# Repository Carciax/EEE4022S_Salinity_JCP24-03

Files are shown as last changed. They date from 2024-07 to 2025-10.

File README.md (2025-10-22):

## The Design of a Salinity Sensor for Antarctic Research
**EEE4022S_Salinity_JCP24-03**
 
This project focused on the design of a salinity sensor for measuring the salinity of the sea water beneath the Antarctica ice caps which had a unique habitat and salinity range due to the ice caps expelling large amount of salt through brine channels into the ocean below. The project consisted of two PCB boards, a probe to be inserted through a drilled hole in the ice and a controller to calibrate, request and display measurements. The probe used a complex switching array to measure the average resistance between a pair of either gold or titanium electrodes using a voltage sweep, then it would calculate the waters conductivity, and finally its salinity.

The salinity sensor probe image

**File Structure**
- EEE4022S 2024 FINAL REPORT CLRCAM007 Clark CF - Pead: The final project report
- CAD: 3D printing files for the pressure sensor waterproof
- Code: The embedded C project code running on the controller and probe boards and the RS485 protocol between them.
- GA Forms: forms required to submit to ECSA
- PCBs: The KiCAD design files for the controller, probe and gold electrode PCBs.
- Presentation: Contains the power point and helper files for the final presentation
- Prototype: The prototype salinity sensor that preceeded this project.
- Report Helper Documents: Documents used for data processing and store from the testing of the probe.
- Report: The LaTeX project file for generating the final report.

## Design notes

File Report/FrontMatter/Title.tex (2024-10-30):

\thispagestyle{empty}
\begin{center}
    
\Huge

\vspace{5cm}

% Title
The Design of a Salinity Sensor for Antarctic Research

\vspace{1cm}

% UCT logo
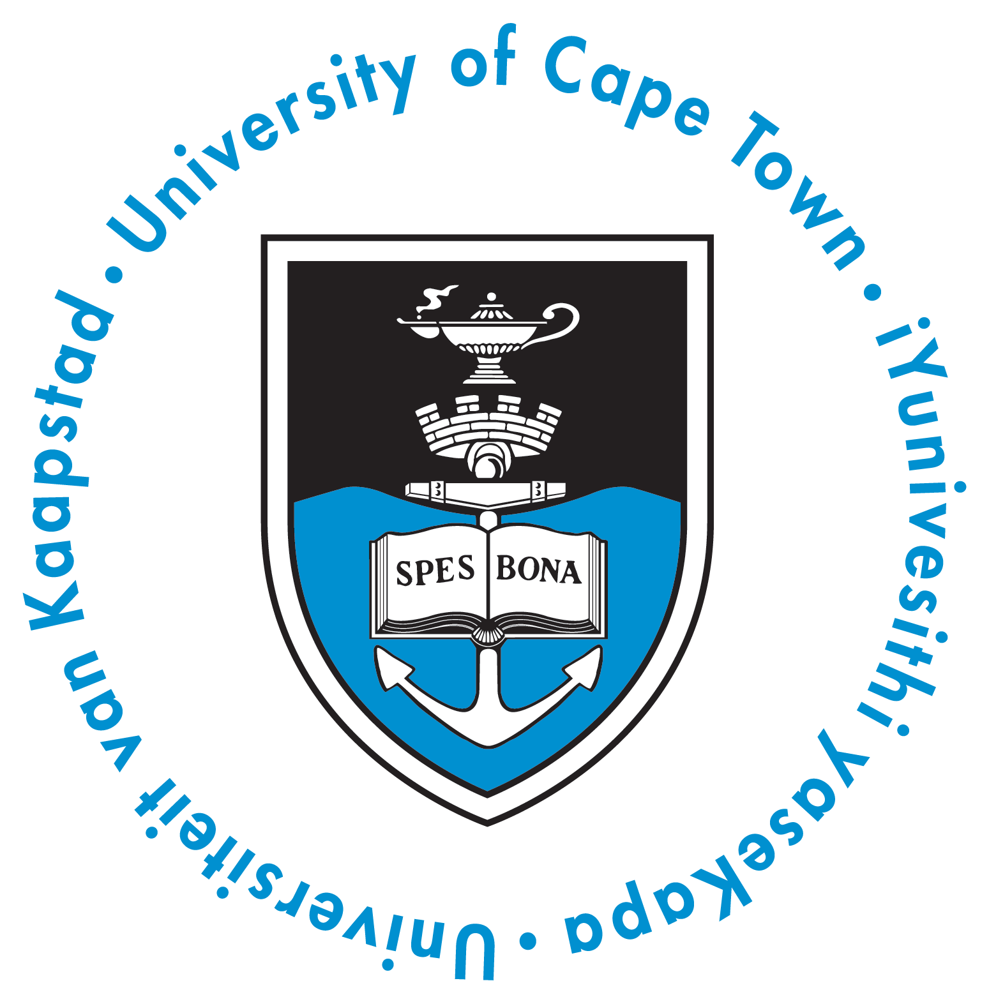
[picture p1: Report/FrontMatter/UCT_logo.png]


\vfill

% My name
\large
\textbf{Prepared by:}\\
Cameron Clark\\
Department of Electrical Engineering\\
University of Cape Town\\

\vspace{1cm}

% My supervisor's name
\textbf{Prepared for:}\\
Justin Pead\\
Department of Electrical Engineering\\
University of Cape Town

\vspace{1cm}

% Today's date
\today

\vspace{1cm}

Submitted to the Department of Electrical Engineering at the University of Cape Town in partial
fulfilment of the academic requirements for a Bachelor of Science degree in Mechatronics

% To add keywords?
\vspace{1cm}
\textbf{Keywords:} Salinity, Sensor, Conductivity, Temperature, Water, Measurement, Electronics, PCB

\end{center}

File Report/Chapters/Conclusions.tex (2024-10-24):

% ----------------------------------------------------
% Conclusions
% ----------------------------------------------------
\chapter{Conclusions}\label{ch:conclusions}

This project presented the development of a prototype electrical conductivity-based sensor and investigated its feasibility.
The prototype was successfully designed and constructed with a separate probe for taking measurements and a controller for user inputs and displaying results.
The probe was able to measure resistance with high accuracy, and it successfully demonstrated a controller-probe communication protocol.

The probe investigated three methods of measuring the electrical conductivity of a solution: voltage sweeps, \gls{ac} voltage, and individual measurements.
Voltage sweep measurements were subject to drift due to the individual measurement altering the solution and affecting the subsequent measurements.
This caused difficulties in determining the salinity of the solution and required further investigation and tests to assess its viability.

\gls{ac} voltage measurements were unsuccessful as the probe was optimised for \gls{dc} measurements, causing the response of the saltwater sample to be interfered with by a capacitor on the probe.
The probe could not be adjusted due to it being cast in epoxy.
Thus, the feasibility of \gls{ac} tests requires further investigation.

Individual measurements were shown to be the most accurate, reporting salinities within $4$ \gls{psu} of the expected value.        
However, this method was vulnerable to noise and errors and has poor repeatability.

In conclusion, this project proved critical concepts of the probe's,  controller's and electrodes' designs and the board-to-board communication.
Additionally, the investigation into the conductivity measurement methods provided valuable insights into the challenges and potential solutions for the probe's future development.

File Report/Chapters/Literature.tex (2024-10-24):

% ----------------------------------------------------
% Literature Review
% ----------------------------------------------------

\chapter{Literature Review}\label{ch:literature}

\section{Introduction}

This literature review starts with introducing the concept of salinity and its history.
It then discusses the importance and various uses of salinity measurements.
The review then covers the various documented methods of measuring salinity, followed by a review of the devices that used conductivity to measure salinity, which is the industry standard.
The review concludes with the theory and calculation of salinity from conductivity measurements.

\section{Salinity Definitions}\label{sec:a-brief-history-of-salinity}
The most commonly understood definition of salinity relates to the total amount of dissolved \textit{salts} in a solution. However, salinity's definition has had several more complex iterations over the last century.
One of the first definitions of salinity was the total amount of dissolved \textit{material} in grams in one kilogram of water~\cite{stewart_introduction_to_physical_oceanography_2004}, which is a dimensionless quantity that was expressed in \gls{ppt} or $g.kg^{-1}$ where most of the ocean water's salinity falls between 34.60\gls{ppt} and 34.80\gls{ppt}~\cite{stewart_introduction_to_physical_oceanography_2004}.

The problem with this definition lies in its testability.
Trying to obtain the mass of the dissolved material through evaporation removed certain compounds, making this method inaccurate~\cite{sverdrup_ocean_physics_and_chemistry_1942} and other methods of isolating the mass of the dissolved material had similar issues~\cite{stewart_introduction_to_physical_oceanography_2004}. 
The need for testability led to salinity being redefined in 1969 to be related to the amount of chlorine present in the water, better known as chlorinity~\cite{stewart_introduction_to_physical_oceanography_2004}.
Chlorinity measurements were well established, and the salinity calculation from chlorinity was relatively simple, which is further discussed in~\refsec{subsec:salinity-from-chlorinity}.

Around the same time as the salinity-chlorinity relationship was established, oceanographers began experimenting with using conductivity to measure salinity.
Conductivity was more precise and straightforward than the titration required to measure chlorinity~\cite{lewis_salinity_definition_and_calculation_1978}.
In 1978, the Practical Salinity Scale was established, which defined salinity in terms of conductivity and is regarded as the current definition of salinity~\cite{lewis_salinity_definition_and_calculation_1978}.
While the conductivity measurement was considered easy, the salinity-conductivity relationship was more complex as it had to include corrections for temperature and depth as they both affect the conductivity of an electrolyte solution~\cite{zheng_electrical_conductivity_of_ocean_2017}.

The Practical Salinity Scale uses dimensionless units of salinity, which are approximately equivalent to \glsreset{ppt}\gls{ppt}~\cite{seabird_ppt_vs_psu_2024} in the current definition of salinity~\cite{ioc_teos_2010}.
Although the Practical Salinity Scale is sometimes given in \gls{psu}, it is more technically correct to refer to it as a certain Practical Salinity `on the Practical Salinity Scale PSS-78'~\cite{lewis_salinity_definition_and_calculation_1978}.
The salinity calculation from conductivity is further discussed in~\refsec{sec:salinity-conductivity-relationship}.

% \section{The Uses of Salinity Measurements}\label{sec:the-uses-of-salinity-measurements}
% oceanography, speciation, conservation, habitation, water quality (drinking, agriculture, industrial), aquaculture, desalination.
% antarctic ice.

\section{Salinity Measurement Methods}\label{sec:salinity-measurement-techniques}

Salinity has had a long history of being measured using various methods with varying degrees of accuracy.
Currently, the most common method of measuring salinity is using a \gls{ctd} instrument. 
However, there are multiple alternative methods, most of which have been developed over the last three decades, a summary of which is provided in \reftbl{tbl:salinity-measurement-methods}.

\begin{longtblr}[
    caption = {Summary of the various methods of measuring salinity.},
    label = {tbl:salinity-measurement-methods},
    ]{
    hlines,
    vlines,
    colspec = {Q[l,m,2.5cm]X[l,m]X[l,m]Q[l,m]}
    }
    \textbf{Method} & \textbf{Key Advantages} & \textbf{Key Disadvantages} & \textbf{Highest Accuracy} \\
    Chlorinity & {\textbullet~Concisely defined \\ \textbullet~Well established} & {\textbullet~Requires titration \\ \textbullet~Has human error} & 0.01\gls{ppt}~\cite{sverdrup_ocean_physics_and_chemistry_1942} \\
    Conductivity & {\textbullet~Industry standard \\ \textbullet~Automated devices available} & {\textbullet~Complex relationship \\ \textbullet~Requires temperature and depth corrections} & 0.0002~\gls{psu}~\cite{seabird_salinity_accuracy} \\
    Density & {\textbullet~Accounts for all dissolved material} & {\textbullet~Complex relationship \\ \textbullet~Requires temperature correction} & 0.003~\gls{psu}~\cite{millero_international_one_atmosphere_eos_seawater_1981} \\
    Microwave Radiation & {\textbullet~Measurable from a distance including from space} & {\textbullet~Requires many corrections \\ \textbullet~Expensive instrument} & 0.1~\gls{psu}~\cite{yueh_microwave_salinity_error_sources_2001} \\
    Refractive Index & {\textbullet~Compact devices available} & {\textbullet~Complex relationship \\ \textbullet~Requires temperature and pressure corrections} & 0.4\gls{ppt}~\cite{malarde_compact_refractometer_2008} \\
    Interferometry & {\textbullet~High accuracy reported} & {\textbullet~Large, complex instrument \\ \textbullet~Difficult to implement} & 0.001~\gls{psu}~\cite{yang_in_situ_refractometer_salinity_measurement_2024} \\
    Electromagnetic Induction & {\textbullet~Non-destructive} & {\textbullet~Not well researched \\ \textbullet~Large, high power instrument} & - \\
\end{longtblr}

\subsection{Salinity from Chlorinity}\label{subsec:salinity-from-chlorinity}

The chemical composition of ocean water with a salinity of 35\gls{ppt} contains 19.35\gls{ppt} of Chlorine and 10.77\gls{ppt} of Sodium with the following most common ions only accounting for just above 3\gls{ppt} of the total dissolved solids in the water~\cite{britannica_seawater_encyclopaedia_2024}.
This allowed oceanographers to determine that the salinity of ocean water was directly proportional to the amount of chlorine in the water, which holds true provided the ratios of the dissolved materials in the water remained constant.
The chlorinity of a solution has an established definition, which is `the mass of silver required to precipitate completely the halogens in $0.328\ 523\ 4 kg$ of the ocean-water sample'~\cite{wooster_redefinition_of_salinity_1969} which could be tested using titration.
In 1969, an accurate relationship between these was established by \refref{wooster_redefinition_of_salinity_1969}, shown in \refeqn{eqn:salinity-chlorinity}, which was significantly more accurate than the evaporation method achieving accuracies within 0.01\gls{ppt}~\cite{sverdrup_ocean_physics_and_chemistry_1942} but was still limited by human error~\cite{lewis_salinity_definition_and_calculation_1978}.
\begin{equation}\label{eqn:salinity-chlorinity}
 S (\text{\gls{ppt}}) = 1.80655 \times~Cl (\text{\gls{ppt}})
\end{equation}

\subsection{Salinity from Conductivity}\label{subsec:salinity-from-conductivity}

The conductivity of a liquid is a measure its ability to conduct electrical current, which is related to the number of free electrons present in the liquid, which is in turn related to the number of ions present in the liquid~\cite{stewart_introduction_to_physical_oceanography_2004}.
In the case of salt water, the ions present are from the dissolved material, which salinity was previously defined on~\cite{stewart_introduction_to_physical_oceanography_2004}.
The relationship between salinity and conductivity accounts for all the ions in the water as opposed to just chlorine which is why it was considered a more apt measure of salinity~\cite{lewis_salinity_definition_and_calculation_1978}.
Measuring conductivity was more accurate than titration, achieving accuracies within $0.0002$ \gls{psu}~\cite{seabird_salinity_accuracy}.
The conductivity measurement is typically done using a \gls{ctd} which measures the conductivity as well as the temperature and depth that are required to accurately calculate salinity.
\Gls{ctd} devices are discussed further in \refsec{sec:salinity-measurement-devices} and the calculation of salinity from conductivity is further discussed in~\refsec{sec:salinity-conductivity-relationship}.

\subsection{Salinity from Density}

The density of pure water varies with temperature and is approximately $1000 kg.m^{-3}$ at $4\degree C$~\cite{USGS_water_density_2018}.
Adding denser materials to the water will intuitively increase its density.
This concept is used to determine the quantity of added material using a density measurement, which can be used to calculate salinity~\cite{kjerfve_salinity_measurement_overview_1983}.
The relationship between salinity and density is approximately linear as shown in \refeqn{eqn:salinity-density} where $\rho$ is the density of the water, $\rho_0$ is the density of pure water, $k$ is a proportionality constant, and $S$ is the salinity of the water~\cite{uow_oceanography_research_1966}.
\begin{equation}\label{eqn:salinity-density}
    \rho = \rho_0(1 + kS)
\end{equation}
The more accurate relationship is more complicated and includes a temperature correction defined by \refref{millero_international_one_atmosphere_eos_seawater_1981}.
While the accuracy of salinity from density was less than that from conductivity with accuracies within $0.003$ \gls{psu}~\cite{millero_international_one_atmosphere_eos_seawater_1981}, \refref{schmidt_density_salinity_relation_2018} still claimed that density was more appropriate to use as the standard potassium chloride solution used to calibrate the \glspl{ctd} meters did not account for the variation of the ratios of conductive and non-conductive materials commonly present in salt water while the density of the water did.

\subsection{Salinity from Microwave Radiation}

The electromagnetic spectrum interacts uniquely with salt water, scattering, refracting, and reflecting when in contact with it or any material dissolved in it.
Different temperature molecules in the water interact with electromagnetic waves differently, and the pressure of the water also varies this interaction. However, the most significant effect is from the presence of the dissolved material~\cite{swift_considerations_for_microwave_salinity_1983}.

Microwave radiation is one section of the electromagnetic spectrum that takes advantage of this fact to measure salinity~\cite{swift_considerations_for_microwave_salinity_1983}.
Microwave radiation does not require direct contact with the water to make a measurement, making it possible to measure the salinity of a water sample from a far distance, including from space~\cite{gabarro_microwave_salinity_2004}.
This necessitated the investigation of the relationship that could accurately predict salinity from a microwave reading~\cite{gabarro_microwave_salinity_2004}.
The relationship required multiple different corrections as the microwave readings were found to be affected by \gls{sst}, surface air pressure, surface air temperature, faraday rotation, and surface wind speed~\cite{yueh_microwave_salinity_error_sources_2001}.

This research has allowed for the development of satellites that can measure the salinity, which has been used to develop global salinity maps as shown in \reffig{fig:satellite_salinity_map}.
The data measured using this method is reported to be accurate to within $0.1$ \gls{psu}~\cite{yueh_microwave_salinity_error_sources_2001}.
\begin{figure}[ht]
    \centering
    
    \caption{Global salinity map generated using satellite data~\cite{esa_mapping_salty_waters_2019}.}
    \label{fig:satellite_salinity_map} %chktex 24
\end{figure}

\subsection{Salinity from Refractive Index}

The second measurement method that takes advantage of the electromagnetic spectrum interaction uses the visible light spectrum to measure the water's refractive index.
The relationship between salinity and refractive index is similarly complex, requiring a 27-term equation that includes the effect of pressure and temperature.
The refractive index equation is defined a range of $500-700nm$ in wave length, $0-30\degree C$ in temperature, $0-40$ \gls{psu}, and $0-11000 dbar$ in pressure, and it holds an accuracy of $0.4-80$ \gls{ppm} \gls{psu}, decreasing with increasing pressure.~\cite{millard_index_of_refraction_algorithm_1990}

Refractometers are used to measures the refractive index of water and as only a small amount of the sample is needed, these devices are relatively compact.
Two notably compact versions have dimensions of $22.5mm \times 22.5mm \times 120mm$~\cite{malarde_compact_refractometer_2008} and $40mm \times 40mm \times 70mm$~\cite{tengesdal_compact_refractometer_2012} which have achieved accuracies of 2 and 83 \gls{ppt} \gls{psu} respectively.

\subsection{Salinity from Interferometry}

The last measurement method that uses the electromagnetic spectrum is interferometry.
Interferometry involves generating two identical light waves on the visible spectrum, passing one through the sample and the other through a non-interfering medium, and then comparing the two waves.
The comparative gain and phase shift between the two waves can be used to identify the salinity of a sample of salt water~\cite{liao_interferometer_seawater_salinity_2023}.

This method has varying implementations, each with varying results.
\refref{yang_in_situ_refractometer_salinity_measurement_2024} reported to be accurate within $0.001$ \gls{psu} using a Michelson interferometer and other researchers have reported other accuracies using different interferometers~\cite{possetti_interferometer_salinity_measurement_2009, nguyen_interferometer_salinity_measurement_2009, zhao_interferometer_salinity_measurement_2009}.
The refractometer has the disadvantage of being a large instrument requiring precisely aligned and spaced mirrors to direct the light waves, making it difficult to implement in a compact device. 

\subsection{Salinity from Magnetic Permeability}\label{subsec:salinity-from-electromagnetic-induction}

Similarly to conductivity, a liquid's magnetic permeability is related to the number of ions present in it.
The more ions present in the liquid, the stronger the magnetic alignment that the liquid can generate, increasing its magnetic permeability.
In salt water, this is related to the total dissolved solids~\cite{somaraju_electromagnetic_salinity_2006}.

Several methods are available for measuring a liquid's magnetic permeability, including \gls{lcr} meters~\cite{waltrip_inductance_measurement_2005}, resonant circuits~\cite{alhassoon_complex_permittivity_extraction_2021}, magnetic force sensors~\cite{pattakos_magnetic_permeability_sensor_2023}, and a permeability bridge~\cite{ewing_magnetic_balance_permeability_1898}.
These methods all have the advantage of not requiring direct contact with the salt water to make a measurement, which allows for the sample to remain undisturbed, unlike conductivity and other methods which may be destructive~\cite{tengesdal_electromagnetic_salinity_2014}.
While the measurement of the magnetic permeability is well-defined, the relationship between it and salinity has yet to be thoroughly investigated.
Additionally, the equipment required to measure the magnetic permeability is relatively large and typically has a high power consumption, making it difficult to compact for use in remote environments.

\section{Salinity Measurement Devices using Conductivity}\label{sec:salinity-measurement-devices}

There are several commercial \gls{ctd} devices available from small handheld devices such as the \href{https://euca.co.za/products/salinity-pen?srsltid=AfmBOorAK21_xoeOZbaqoqXbRzrLxF5Yx47nzn7tvsve-_Azl3sSh1-QbIg}{Salinity Pen} to large oceanographic research devices such as \href{https://oceanexplorer.noaa.gov/technology/ctd/ctd.html}{Ocean Exploration's CTD}.
These devices are used in various applications with varying prices and accuracies. 
The fundamental concept of the device involves placing two electrodes in a sample of water, applying a voltage across them, and measuring the water's response.
This is paired with a temperature and depth correction, which allows a salinity value to be calculated, which is discussed in \refsec{sec:salinity-conductivity-relationship}.
Unfortunately, most of \gls{ctd}'s technology is proprietary so the exact workings of their devices are not published.

Some researchers have developed their own \gls{ctd} devices for specific applications.
A study investigating the effect of human activities that alter the salt concentration of water sources such as lakes, ponds and wetlands in Illinois, USA, developed their own \gls{ctd}.
The device reported an average error of 6\% in the laboratory validation and 11\% in the field validation.
It used an alternative approximation of converting the conductivity to salinity, which used single voltage readings to measure the resistance of the water samples, which were then used to create a sensor-specific mathematical model to convert the resistance to salinity~\cite{benjankar_ec_based_salt_measurement_2021}.
The voltage readings showed a non-linear relationship with between resistance and voltage, similar to that covered by \refref{ostdiek_inquiry_into_physics_2020}.
A similar device was shown on a forum with a similar design principle; however, this one was significantly less advanced, making no attempt to correlate the measured resistance values to a salinity value~\cite{instructables_water_salinity_meter}.

Researchers at Uppsala University in Sweden developed a nano \gls{ctd} probe that measured $7.5 \times 3.5mm$ in size, shown in \reffig{fig:nano-ctd}.
The probe contained everything required for an accurate salinity measurement, and each of the sensors achieved a high degree of accuracy.
The probe achieved a high $r^2$ value of $0.9787$ and a standard deviation of 2.37\gls{ppt} using an alternating current at 42kHz to measure the conductivity.
This design indicated that miniaturized salinometers are viable and could be used in devices such as bio-loggers on marine animals.~\cite{jonsson_chip_based_salinity_2013}
\begin{figure}[ht]
    \centering
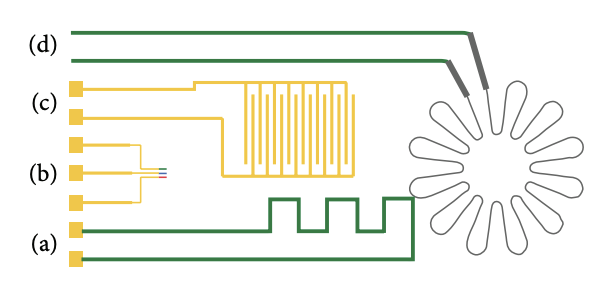
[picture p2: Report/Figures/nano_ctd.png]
    
    \caption{The schematic of a \gls{ctd} probe developed by researchers at Uppsala University in Sweden which design contains (a) a temperature sensor, (b) three relatively small electrodes for pH and Cl- concentration, (c) conductivity electrodes, and (d) a strain gauge for the pressure membrane sensor. The design is $7.5 \times 3.5 mm$ in size~\cite{jonsson_chip_based_salinity_2013}.}
    \label{fig:nano-ctd} %chktex 24
\end{figure}

% CTDs, refractometers, conductivity meters, salinometers.

% ----------------------------------------------------
%current CTDs
%
%electrical conductivity sensor https://link.springer.com/article/10.1007/s11270-020-04971-7
%
%arduino version https://www.instructables.com/Water-Salinity-meter/
%
%mini version https://www.diva-portal.org/smash/get/diva2:512332/FULLTEXT01.pdf
%
%% ----------------------------------------------------
%measurement techniques
%
%high res https://link.springer.com/chapter/10.1007/978-1-4615-9182-5_18
%
%salinity and its measurands https://iopscience.iop.org/article/10.1088/1681-7575/aaea92/pdf
%
%interferometer https://iopscience.iop.org/article/10.1088/0957-0233/20/3/034003/meta?casa_token=ZTZbYNUpO0kAAAAA:7jvq44f2kE5qGGEQWt5ji18A7xWG4p9ZT4Ny99eOjMPOfywPIgqRNoCeH0VZby1VjlART_v77WV3rxfwi0k1nwphxfguYA
%
%the whole suite, important for later https://www.researchgate.net/profile/Bjoern-Kjerfve/publication/255660361_Measurement_and_Analysis_of_Water_Current_Temperature_Salinity_and_Density/links/0c9605373c5d3088b4000000/Measurement-and-Analysis-of-Water-Current-Temperature-Salinity-and-Density.pdf
%
%microwave frequency https://www.sensorsportal.com/HTML/DIGEST/january_2014/Vol_162/P_1772.pdf
%
%refraction of light https://www.sciencedirect.com/science/article/abs/pii/S0925400503002922?casa_token=UDq5jm83UIsAAAAA:-UuQMhyBg9tuzleSc8tQnL2vuCv_HYHCB5AicHCTlBkBz_5gipNnDoA6DdPgBL9csU_wWS9lG6Bc
%
%conductivity using electromagnetism https://ieeexplore.ieee.org/abstract/document/7769877
%
%salinity equation paper https://agupubs.onlinelibrary.wiley.com/doi/abs/10.1029/jc083ic01p00466?casa_token=Om_oxKhUgLIAAAAA%3As_ZdT6Qn-zv9SSyC8G3io5r_0mxuepRxFE33jcaLtTNY4tyOQOLAObVtsjeQZ0gPpokwsmrEOP0pPHULQg
%
%% ----------------------------------------------------
%salinity properties
%
%temperature vs salinity https://link.springer.com/article/10.1023/B:EMAS.0000031719.83065.68
%
%salinity and other properties https://pubs.acs.org/doi/10.1021/es402188r
%
%salinity and it antecedents https://ieeexplore.ieee.org/stamp/stamp.jsp?tp=&arnumber=1145448
%
%salinity textbook https://pubs.acs.org/doi/pdf/10.1021/ja02205a013?casa_token=QPyPLh22vacAAAAA:O6Hc1M5FQEDZpJb4oUrGYzboIy0wWn__w6MxXGc8Aw7doPE9tz71yRCbmUtRSP5lOMdTr28U8bYI43IsBg
%
%electrical properties of salt ice https://pubs.acs.org/doi/full/10.1021/jp8055366?casa_token=qvssn_P9p_8AAAAA%3A1FY_4CW5oX_4P9gDNZfp0AaeByCkTF_WOcZ_hLbv2Y2FYsIRsO7ZZkqxzTHTo_MK4vWqfaqqQh2LagyDLA
%
%pressure and temperature increase conductivity https://journals.aps.org/pr/abstract/10.1103/PhysRev.70.329
%
%conductivity vs total dissolved solids https://iopscience.iop.org/article/10.1088/1755-1315/118/1/012019/meta
%
%% ----------------------------------------------------
%producers or CTDs
%
%https://www.whoi.edu/what-we-do/explore/instruments/instruments-sensors-samplers/conductivity-temperature-depth-ctd-sensors/
%
%% ----------------------------------------------------

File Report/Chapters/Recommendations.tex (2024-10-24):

% ----------------------------------------------------
% Recommendations
% ----------------------------------------------------

\chapter{Recommendations}\label{ch:recommendations}

Further investigation of the methods of conductivity measurements was required.
The voltage sweep method was vulnerable to individual measurements when adjusting the saltwater sample.
To avoid this, using a water pump to circulate the water during the measurement is recommended.
This setup would require a large volume of water of known salinity to be used, which would present additional challenges when calibrating the probe with the $35$ \gls{psu} standard solution at $15\degree C$ and $0dbar$.

The probe was not designed for measuring \gls{ac} voltages.
However, altering the probe to remove the capacitor that was likely interfering with the measurement would allow for a further investigation into \gls{ac} voltage's feasibility.
Additionally, a future iteration of the probe could be explicitly designed to measure \gls{ac} voltages and determine its feasibility.

The attachment of the gold electrodes to the probe \gls{pcb} was suboptimal, breaking on two occasions during the project.
An alternative method of attaching them would be using a slot joint~\cite{nicolaas_slot_joint_2015}, where a slot could be cut into the probe and the electrodes, allowing them to slide into each other and be soldered in place on both sides, which would potentially be more robust.
This design would make it challenging to have more than two connections to the electrode, but it could allow the probe to be thinner and taller, allowing it to fit down a smaller diameter ice core.

The controller proved successful in all its requirements, but a more user-friendly interface and housing would benefit the final device.
A housing could be 3D printed to make the device easier to handle, more aesthetically pleasing, and protect it from the elements.
Additionally, the 7-segment displays could be replaced with a \gls{lcd}, allowing for more detailed and clear information to be displayed to the user.

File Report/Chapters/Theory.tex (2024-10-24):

% ----------------------------------------------------
% Theory Development
% ----------------------------------------------------

\chapter{Theory Development}\label{ch:theory-development}

\section{The Calculation of Salinity From Conductivity}\label{sec:salinity-conductivity-relationship}

Salinity meters that use electrical conductivity are commonly known as \glspl{ctd}.
As depth is a measurement derived from pressure, CTp is the preferred designation when performing calculations~\cite{lewis_salinity_definition_and_calculation_1978}, which allows for the conductivity of a sample of water to be denoted by $C(S, T, p)$ where conductivity is a function of salinity $S$, temperature $T$, and pressure $p$ which is the convention in oceanography~\cite{lewis_salinity_definition_and_calculation_1978}.
Pressure in the salinity equation is taken relative to sea level where $p = 0 dbar$ is equivalent to an absolute pressure of $P = 101\ 325 Pa$~\cite{ioc_teos_2010}.
Using decibars (dbar) for pressure is a common practice in oceanography as it is a unit of pressure roughly equivalent to one meter of water depth~\cite{seabird_dbar_to_depth_2024}.

The Practical Salinity Scale defines Practical salinity $S_p$ in terms of a conductivity ratio $K_{15}$, which is the conductivity of a sample of water at a temperature of $15\degree C$ and a pressure equal to one standard atmosphere divided by the conductivity of a standard potassium chloride solution at the same temperature and pressure.
The standard potassium chloride solution is $32.4356g$ of $KCl$ dissolved in $1.000kg$ of water, and when the ratio between the conductivity of a sample of water and the standard solution, or $K_{15}$, equals 1, the Practical Salinity $S_p$ is, by definition, 35.~\cite{ioc_teos_2010}

When $K_{15}$ is not equal to 1, the Practical Salinity $S_p$ can be calculated using the PSS-78 equation shown in \refeqn{eqn:pss-78-k15}.
\begin{equation}\label{eqn:pss-78-k15}
 S_p = \sum_{i=0}^{5} a_i {(K_{15})}^{i/2}~~~~\text{where}~~~~K_{15} = \frac{C(S_p, 15\degree C, 0)}{C(35, 15\degree C, 0)}
\end{equation}
All the coefficients for the salinity-conductivity equations, including $a_i$, are given in~\reftbl{tab:pss-78-coefficients}.

To calculate the salinity of a sample of water that is not at $15\degree C$ and $0 dbar$, the conductivity ratio of the sample can be expanded into the product of three ratios, which are labelled $R_p$, $R_t$, and $r_t$ respectively.
The conductivity measurement taken in the field $C(S_p, t, p)$ is related to the conductivity of the standard solution $C(35, 15\degree C, 0)$ which the device is calibrated with and is represented by $R$ in \refeqn{eqn:pss-78-full-ratio}.~\cite{ioc_teos_2010}
\begin{equation}\label{eqn:pss-78-full-ratio}
 R = \lfrac{C(S_p, t, p)}{C(35, 15\degree C, 0)} = \lfrac{C(S_p, t, p)}{C(S_p, t, 0)} \cdot \lfrac{C(S_p, t, 0)}{C(35, t, 0)} \cdot \lfrac{C(35, t, 0)}{C(35, 15\degree C, 0)} = R_p R_t r_t
\end{equation}
\textit{check}
In order to calculate the salinity of the sample, $R_t$ must be found, which takes a similar form to $K_{15}$.
$r_t$ is first calculated using the temperature of the sample 
\begin{equation}\label{eqn:pss-78-rt}
 r_t = \sum_{i=0}^{4} c_i {t}^i
\end{equation}
following which $R_p$ is calculated using the sample's pressure $p$, temperature $t$ and conductivity ratio $R$,
\begin{equation}\label{eqn:pss-78-rp}
 R_p = 1 + \lfrac{\sum_{i=1}^{3} e_i p^i}{1 + d_1 t + d_2 {t}^2 + R\left[ d_3 + d_4 t \right]}
\end{equation}
and finally $R_t$ is calculated using $r_t$, $R_p$ and $R$.
\begin{equation}\label{eqn:pss-78-Rt}
 R_t = \lfrac{R}{R_p r_t}
\end{equation}
For a sample temperature of $15\degree C$ and pressure of $0 dbar$, $r_t$ and $R_t$ both equal 1, which leaves $R_t$ equal to $R$ and thus \refeqn{eqn:pss-78-k15} can be used to calculate the Practical Salinity $S_p$.
For temperatures other than $15\degree C$, the Practical Salinity $S_p$ can be calculated using \refeqn{eqn:pss-78-full} where $k = 0.0162$.~\cite{ioc_teos_2010}
\begin{equation}\label{eqn:pss-78-full}
 S_p = \sum_{i=0}^{5} a_i {(R_t)}^{i/2} + \lfrac{t-15}{1+k(t-15)} \sum_{i=0}^{5} b_i {(R_t)}^{i/2}
\end{equation}

% chktex-file 44    
\begin{longtblr}[
 caption = {Coefficients for the PSS-78 equations~\cite{ioc_teos_2010}.},
 label = {tab:pss-78-coefficients}
 ]{
 colspec = {|q{1.5cm}|C|C|C|C|C|}
 }
    \hline
    \textbf{$i$} & \textbf{$a_i$} & \textbf{$b_i$} & \textbf{$c_i$} & \textbf{$d_i$} & \textbf{$e_i$} \\
    \hline
    $0$ & $0.0080$ & $0.0005$ & $6.766097\e{-1}$ & & \\
    \hline
    $1$ & $-0.1692$ & $-0.0056$ & $2.00564\e{-2}$ & $3.426\e{-2}$ & $2.070\e{-5}$ \\
    \hline
    $2$ & $25.3851$ & $-0.0066$ & $1.104259\e{-4}$ & $4.464\e{-4}$ & $-6.370\e{-10}$ \\
    \hline
    $3$ & $14.0941$ & $-0.0375$ & $-6.9698\e{-7}$ & $-4.215\e{-3}$ & $3.989\e{-15}$ \\
    \hline
    $4$ & $-7.0261$ & $0.0636$ & $1.0031\e{-9}$ & $-3.107\e{-3}$ & \\
    \hline
    $5$ & $2.7081$ & $-0.0144$ & & & \\
    \hline
\end{longtblr}
Note that the coefficients $a_i$ precisely sum to 35 such that the Practical Salinity $S_p$ is 35 when $K_{15}$ or $R_t = 1$ as per \refeqn{eqn:pss-78-k15} and \refeqn{eqn:pss-78-full}.
Additionally, the coefficients $b_i$ precisely sum to 0 such that the Practical Salinity $S_p$ does not depend on the temperature of the water when $R_t = 1$ as per \refeqn{eqn:pss-78-full}.~\cite{ioc_teos_2010}

\refeqn{eqn:pss-78-k15} to \refeqn{eqn:pss-78-full} are valid for $2 < S_p < 42$ and $-2\degree C < t < 35\degree C$ and $0 dbar < p < 10\ 000 dbar$~\cite{ioc_teos_2010}.
The range for salinity has been extended using estimations by \refref{hill_extension_of_pss_low_1986} for $0 < S_p < 2$ and \refref{poisson_extension_of_pss_high_1993} for $42 < S_p < 50$.

The temperatures used in \refeqn{eqn:pss-78-k15} to \refeqn{eqn:pss-78-full} are on the IPTS-68 scale~\cite{furukawa_ipts68_1973} and have not been corrected to the currently used ITS-90 scale~\cite{preston_its90_1990}. 
In order to correctly calculate the salinity, the temperatures should be converted to the IPTS-68 scale using the equation $t_{68} = 1.00024 t_{90}$ before calculating salinity~\cite{preston_its90_1990}.

% \section{Electrical Characteristics of Salt Water}\label{sec:electrical-characteristics-of-salt-water}
% PSU vs TSD vs conductivity vs resistivity, salinity equation, capacitance of salt water, non-constant conductivity vs voltage.

% \section{External Factors Affecting Electrical Characteristics of Salt Water}\label{sec:external-factors-affecting-electrical-characteristics-of-salt-water}

% \section{Salt water's Resistance-Voltage Measurement}
% ostdiek_inquiry_into_physics_2020

\section{Current Fringing in Conductive Materials}

Current fringing or current spreading, not to be confused with magnetic fringing, occurs when an electrical current flowing through a conductive material spreads like a magnetic field.
This is a phenomenon that is particularly prevalent and well studied in the manufacturing of \glspl{led} where the current spreading can be a significant factor in the efficiency of the device~\cite{solomentsev_LED_current_spreading_2022, hwang_LED_current_spreading_2008, jeon_LED_current_spreading_2001}.

The effect of current spreading in typical conductors is mostly negligible; if the material's conductivity is high enough and its cross-sectional area is small, the current spreading is minimal.
However, if a conductor has a significantly larger cross-sectional area than the current requires, such as electrodes in salt water, the current spreading can become a significant factor in its conductivity.
This version of current spreading has been studied and is documented for conductors of constant conductivity.~\cite{jason_current_spreading_long_objects_2008}

% \section{Electromagnetic Interference of Salt Water}

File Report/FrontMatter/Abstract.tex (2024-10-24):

\chapter*{Abstract}
The Antarctic ice shelves are a habitat that supports numerous unique species in and below the ice.
Melting ice causes salt to be expelled, which drains into the ocean beneath, creating a mixing zone with properties that are currently being investigated.
A prototype electrical conductivity-based salinometer was developed for this project to replace the current method of measuring the salinity of the mixing zone.
The prototype was designed with a separate probe, which would be lowered through a hole in the ice to the ocean below, and a controller, which would request and display data from the probe.
The probe utilised two types of electrodes made from gold and titanium to investigate the methods of measuring repeatable and accurate salinity measurements.
Voltage sweeps and \gls{ac} voltages could not produce accurate results as they needed further apparatus and investigations.
Single voltage measurements were able to calculate salinities to within $4$ \gls{psu} of the expected value but were vulnerable to noise and other errors.

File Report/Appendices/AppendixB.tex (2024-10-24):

\chapter{Graduate Attribute Assessment}\label{appx:gaassessment}

\begin{longtblr}[
    caption = {Graduate Attribute Assessment},
    ]
    {
        hlines,
        vlines,
        colspec = {Q[c,m]Q[c,m,3cm]X[c,m]},
    }
    \textbf{GA} & \textbf{Requirement} & \textbf{Justification and section in the report}  \\
    1 & Problem-solving & This project solved the problem of designing a compact salinity meter which included circuit, \gls{pcb} and board-to-board communication design and embedded C coding in \refch{ch:design}. \\ 
    4 & Investigations, experiments and data analysis & This project investigating the properties of saltwater conductivity measurements and evaluated the performance of the probe in \refch{ch:testing}.\\
    5 & Use of engineering tools & This project used KiCad software to design and fabricate \glspl{pcb}, FreeCAD and PrusaSlicer to 3D print switch caps, and Microsoft Excel and MATLAB to conduct data analysis in \refch{ch:design},~\ref{ch:implementation} and~\ref{ch:testing} respectively.\\
    6 & Professional and technical communication & This project demonstrated professional and technical communication through the writing of a report covering the project. \\
    8 & Individual work & This report covers the individual report conducted by its author in the research, design, implementation and testing of a prototype salinometer in \refch{ch:literature},~\ref{ch:design},~\ref{ch:implementation} and~\ref{ch:testing} respectively. \\
    9 & Independent learning ability & This report demonstrates the independent learning ability its author through the research in \refch{ch:literature} conducted and applied to the design of a salinometer in addition to the iterative testing conducted in \refch{ch:testing}. \\
\end{longtblr}

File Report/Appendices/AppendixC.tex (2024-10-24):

\chapter{Git Repository}\label{appx:gitrepo}

\href{
    https://github.com/Carciax/EEE4022S_Salinity_JCP24-03
}{
    Link
}

\begin{longtblr}[
    caption = {Git Repository Contents},
    ]
    {
        hlines,
        vlines,
        colspec = {Q[c,m]X[c,m]},
    }
    \textbf{Folder} & \textbf{Contents} \\
    PCBs & The design of the probe, controller and gold electrode \glspl{pcb}. \\
    Code & The code for the probe and controller \glspl{pcb} and the communication between them. \\
    Report & The \LaTeX code for this report. \\
    Report Helper Documents & Files for creating graphs and images for this report and storing the results of the tests conducted. \\
    CAD & The files for the switch caps.\\
    GA Forms & The forms for submitting the graduate attribute assessment. \\
\end{longtblr}

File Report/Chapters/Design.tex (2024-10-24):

% ----------------------------------------------------
% Design
% ----------------------------------------------------

\chapter{Design}\label{ch:design}

\section{Salinity Measurement Method}

The industry standard for measuring conductivity is the \gls{ctd}, which calculates salinity using conductivity, temperature and depth measurement.
\refsec{sec:salinity-measurement-techniques} discussed several alternative methods of measuring salinity.
The temperatures, environment and remote nature of the Antarctic make most of these methods difficult or impossible to use.
Additionally, the final device was required to fit through an ice core hole of $110mm$ in diameter.
While the prototype does not need to directly meet this requirement, it must be designed such that a future iteration that can.

Refractometers and chlorinity titrations have the same drawbacks as the currently used hand-held \gls{ctd}, where capturing a water sample and bringing it to the surface alters its temperature and pressure, which may alter its salinity measurement.
Microwave radiation has a lower-than-desirable accuracy.
In addition, the instruments that measure it, as well as densitometers and interferometers, are expensive and complex beyond the author's expertise.
Electromagnetic induction is one of the more promising methods because it is a nondestructive method of measuring salinity, which allows samples to be used for alternative measurements afterwards.
However, as mentioned in \refsec{subsec:salinity-from-electromagnetic-induction}, the electromagnetic and salinity relationship has yet to be thoroughly researched, and it requires a high power consumption.
This latter is a significant issue in Antarctica as storing power is challenging at very low temperatures, not to mention transporting the device.

The conductivity, temperature and depth method was determined to be the most viable for this project as it is the industry standard, and the author has significant experience with \gls{pcb} design and electronics.
Additionally, it has been proven that it can be miniaturized, as mentioned in \refsec{sec:salinity-measurement-devices}, making it the most likely method to fit through the ice core.
This and the other methods face a challenge because the Practical Salinity Scale is not defined for sub-zero temperatures, which may be a problem in Antarctica and should be researched further.

\section{Conductivity Electrode Material}

Ideal electrodes for measuring conductivity in salt water have zero resistance and infinite corrosion resistance and can confine the electrical current in the water to a specific known volume.
Electrodes with zero resistance would allow the resistance measured using the electrodes to be entirely due to the water.
However, most conductive materials have a conductivity in the order of $10^8 Sm^{-1}$, which causes negligible resistance compared to salt water which has a conductivity range of $0-5 Sm^{-1}$~\cite{as_typical_conductivity_2022}.
The infinite corrosion resistance will allow the electrodes to last indefinitely in the highly corrosive saltwater environment, and several materials with near-perfect corrosion resistance are used in marine environments, which will be able to satisfy this criterion.
The confinement of the electrical current allows for an easier calculation of the conductivity $\rho$ from resistance $R$ if the cross-sectional area $A$ and length $l$ of the water between the electrodes is known as shown by \refeqn{eqn:conductivity-from-resistance}.
\begin{equation}
    \rho = \lfrac{RA}{l}
    \label{eqn:conductivity-from-resistance}
\end{equation}
Several materials known for their corrosion resistance include non-precious metals such as aluminium, stainless steel, nickel and copper alloys, and titanium, as well as precious metals such as gold, silver, and platinum.
Precious metals are known for having a significantly higher corrosion resistance. 
However, they are also significantly more expensive.

Choosing the electrode's material involved prioritising high corrosion resistance and low resistance while being restricted to materials that were attainable and within this project's budget.
Titanium is the most corrosive resistant of the non-precious metals and has an acceptable conductivity of $2,3\e{6}$ which is about $25$ less than that of copper~\cite{walsh_electrodes_conductivity_1991}.
Titanium wire was available through off-cuts from a project being conducted by the Chemical Engineering Department of the University of Cape Town. 
Thus, it was possible to use this material for the electrodes.

Of the precious metals, gold is one of the most accessible as it is a common material used in \glspl{pcb} manufacturing primarily because of its high corrosion resistance paired with a high conductivity of $49\e{6}$ which is similar to copper's conductivity~\cite{walsh_electrodes_conductivity_1991}.
\gls{enig} \gls{pcb} manufacturing is a process where nickel, followed by gold, is deposited onto the copper of the \gls{pcb} using chemical reactions.
While this process is expensive compared to standard \gls{pcb} manufacturing, it is affordable within this project's budget and made gold a possible electrode material.

Both gold and titanium were used for this project, as they could be manufactured into electrodes of different shapes, which allowed for comparative testing of the materials and the shapes.
The electrode design is further discussed in \refsec{sec:conductivity-electrode-design}.

\section{Conductivity Electrode Design}\label{sec:conductivity-electrode-design}

Gold electrodes made using the \gls{enig} \gls{pcb} manufacturing process were chosen as the device's primary electrodes.
The \gls{pcb} manufacturing process allowed the electrodes to be made with a known area and length of the water between the electrodes, allowing for a more accurate conductivity calculation.

Salt water does not have a constant resistivity with respect to voltage~\cite{benjankar_ec_based_salt_measurement_2021},\cite{mccomas_inquiry_into_physics_2005}.
In order to isolate the non-linear resistance-voltage curve, the resistance of the water between the electrodes needed to be measured at different voltages while other factors were kept constant.
This necessitated close attention to the fringing effect of the electrical current between the electrodes.
Wide, flat pads were used on the \gls{pcb} electrodes, which were placed close together to reduce the current spreading.
Additionally, a fringe guard was added to the electrodes, which consisted of a pad that outlined the main conductivity pads that repeated the same voltage as the main pads using an op-amp with unity gain.
Ideally, the fringe guard would saturate the volume around the main pads with current and thus prevent them from fringing.
\gls{pcb} connectors to attach the electrodes to a probe were added to this configuration, as shown in \reffig{fig:gold-electrode}.

%chktex-file 44
\begin{figure}[ht]
    \begin{minipage}{0.5\textwidth}
        
    \centering
    
\end{minipage}
\begin{minipage}{0.5\textwidth}
    \begin{tabular}{cl} \hline
        1 & \gls{pcb} Connectors \\ \hline
        2 & $2mm$ Fringe Guard \\ \hline
        3 & $20mm \times 20mm$ Main Pad \\ \hline
    \end{tabular}
\end{minipage}
    \caption{The gold electrode \gls{pcb} design.}
    \label{fig:gold-electrode} %chktex 24
\end{figure}

The dimensions of the gold electrodes were chosen to be round values, with the pads having a large surface area and being placed relatively close together.
However, they could not be placed too close together as this could prevent water from effectively flowing between them.
Theoretically, this would reduce the proportion of fringing versus linear current between the electrodes.
This theory is based on the electrical field fringing effect found in capacitors: take two capacitor pads that are placed close together, which experience a certain amount of fringing; if the area of those two pads increases, the quantity of fringing field will increase relative to the side length while the quantity of linear field which would increase relative to the square of the side length~\cite{hegg_capacitor_electric_fringing_2004, sloggett_fringing_fields_in_disc_1986}.

The second method employed to reduce the fringing effect was to keep the resistance between the pads low, which lowers the voltage required to generate a current through the water, which would theoretically further reduce the current fringing.
This theory is also based on capacitors where higher voltages generate stronger electrical fields that spread, or fringe, more.

The gold electrodes were designed with a $20mm \times 20mm$ main pad with a $2mm$ wide fringe guard surrounding it and a spacing between the electrodes of $10mm$.
The expected resistance was then calculated to be between $3,75\Omega$ and $6,25\Omega$ using \refeqn{eqn:conductivity-from-resistance} and conductivity values for salinities between $40$ and $25$ \gls{psu}~\cite{ioc_teos_2010}.

The titanium electrodes were less complicated to design as they only had two variable parameters: their length and spacing.
However, as they were made from titanium wire, the fringing effect between them could not be reduced using the same method as the gold electrodes.
Thus, it was decided to use the gold electrode to evaluate an accurate method for determining conductivity, which could then be applied to the titanium electrodes, where the fringing effect could be mathematically corrected.

The titanium electrodes are significantly more cost-effective than the gold electrodes. 
Thus, if an accurate method for determining salinity using them is developed, they will likely become the primary electrodes of the final device.  
The titanium wire available for this project was $1mm$ in diameter and to account for the unknown resistance between the electrodes, the design allowed for adjustable spacing between the electrodes and adjustable electrode length.

\section{Resistance Measurement Method}

The most common and practical method of measuring resistance is using a resistor divider circuit, which this project chose to employ. 
While current measuring \glspl{ic} exist, the low current ($<1A$) versions use the same resistor divider principle. 
Thus, it was considered to be more cost-effective and configurable to design the resistor divider circuit.

The electrodes were chosen to be the $R_2$ resistor in the voltage divider, and the $R_1$ resistor was chosen to be a significantly larger, known resistance.
The large $R_1$ value allowed a full range of voltages to be applied to the resistor divider while keeping the voltage across the electrodes low, which was advantageous for the reasons mentioned in \refsec{sec:conductivity-electrode-design}.
This configuration also prevented the circuit from being short-circuited if the electrodes were to touch, as the $R_1$ resistor would limit the current.
The voltage drop across the electrodes was then amplified using an op-amp to increase the resolution of the voltage measurement.

\section{Circuit Overview}

The resistor divider circuit was designed to be printed onto a \gls{pcb} (herewith referred to as the probe) manufactured with JLCPCB.
\gls{pcb} manufacturing is cost-effective, has a high precision relative to hand soldering, and the process was familiar to the author, making it the ideal method for creating the prototype.
However, the resistor divider circuit required a few additions to increase its versatility and testing capability, an overview of which is shown in \reffig{fig:circuit-overview}.

\begin{figure}[ht]
    \centering
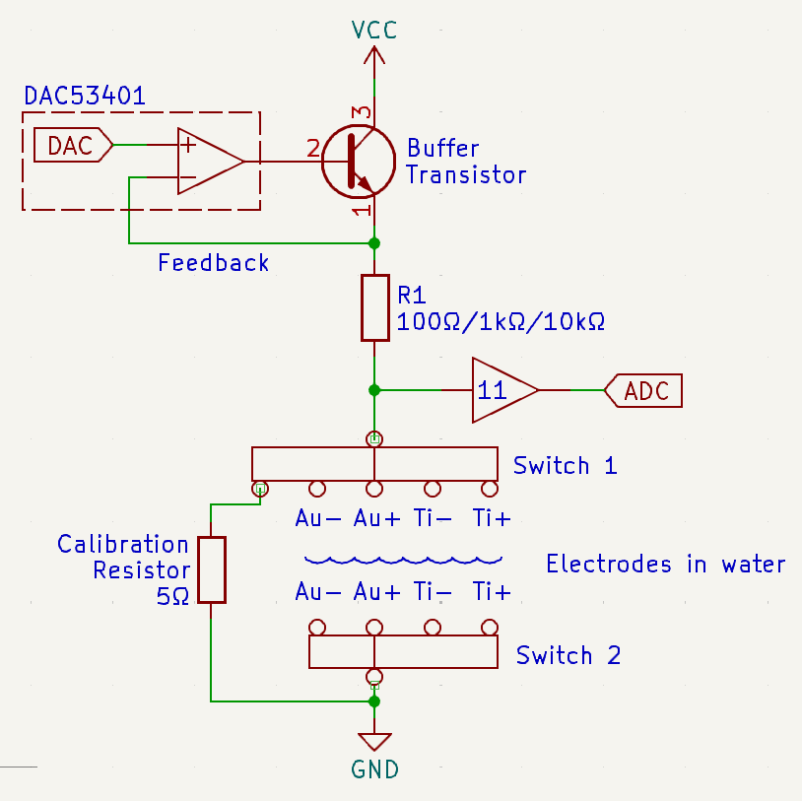
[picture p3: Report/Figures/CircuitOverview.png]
    
    \caption{A simplified representation of the resistance measuring circuit.}
    \label{fig:circuit-overview} %chktex 24
\end{figure}

The voltage driving the resistor divider was provided by a \gls{dac} so that the voltage could be varied and salt water's voltage-resistance relationship could be determined.
The \gls{dac} model was chosen from the \glspl{dac} available on the JLCPCB's website.
The model DAC53401 was ultimately chosen for its high updated time of $10us$ and its advanced functionality, which allowed it to output square, triangle, and sawtooth waves.
This functionality could be used to perform high-frequency tests in addition to linear voltage sweeps.

A typical configuration of a \gls{dac} is to connect its output to the non-inverting input of an op-amp, which would be connected to the base of a transistor.
The transistor's emitter would then be connected to the inverting input of the op-amp.
This configuration allows a higher current to be drawn than the \gls{dac} can provide while maintaining the specified output voltage.
The DAC53401 has an internal op-amp and a feedback input, which allows a transistor to be connected as shown in \reffig{fig:circuit-overview} to achieve the same outcome.

Sets of switches added to the circuit allowed the voltage produced by the \gls{dac} to be directed to an $R_1$ resistor, then across to a pair of electrodes or to a calibration resistor.
The switch model TS3A4751 was chosen from JLCPCB, which contained four switches in its \gls{ic}, as it was very cost-effective for its low and consistent on-state resistance of around $0.7\Omega$.
The circuit required three switching points: one for choosing the $R_1$ resistor, one for choosing the anode and one for choosing the cathode.

It was decided to give the $R_1$ resistor alternate resistances to allow for any possible resistance between the titanium electrodes or unforeseen errors.
The $R_1$ value chosen to pair with the gold electrodes was $100\Omega$ as it was the smallest e12 series resistance that would prevent the board from drawing too much current and burning out the traces or switches.
The final resistances were chosen to be $100\Omega$,  $1k\Omega$ and $10k\Omega$, which would be used when the resistance between the probes was $1\Omega - 10\Omega$, $10\Omega - 100\Omega$ and $100\Omega - 1k\Omega$ respectively.
This configuration allowed for a minimum resolution of $11\%$ of $V_{DAC}$ for the voltage measurement by the \gls{adc} as shown by \refeqn{eqn:adc-resolution}.
\begin{align}\label{eqn:adc-resolution}
 \lfrac{1\Omega}{1\Omega + 100\Omega} * V_{DAC} * 11 = 11\%V_{DAC} \\
 \lfrac{10\Omega}{10\Omega + 100\Omega} * V_{DAC} * 11 = 100\%V_{DAC}
\end{align} 

The anode switch, denoted as switch 1 in \reffig{fig:circuit-overview}, allowed $R_1$ to be connected to any of the four electrodes or to the calibration resistor of $5\Omega$, and the cathode switch, denoted as switch 2 in \reffig{fig:circuit-overview}, allowed any electrode to be connected to ground.
An example of measuring the resistance between the titanium electrodes would be to connect switch 1 to Ti+ and switch 2 to Ti, allowing the voltage drop to be measured.
This configuration also allows current to flow in both directions between electrodes, which can prevent an excessive buildup of chlorine gas or sodium electroplating on the electrodes or electrolysis of the water by taking a resistance measurement in both directions in rapid succession.

To increase the accuracy of the $R_1$ resistors, they were made by placing multiple high-accuracy resistors in parallel, which decreases their resistance uncertainty.
The total uncertainty of the parallel resistance $\delta_{R_{total}}$ is decreased by a factor equal to number of parallel resistors $n$ compared to each resistance's uncertainty $\delta_R$ as shown by \refeqn{eqn:parallel-resistor-total} to \refeqn{eqn:parallel-resistor-uncertainty}.
\begin{gather}
 R_{total} = {\left[ \sum_{i=1}^{n} \lfrac{1}{R} \right]}^{-1} = {\left(\lfrac{n}{R}\right)}^{-1} = \lfrac{1}{n}\cdot R \label{eqn:parallel-resistor-total} \\
 \text{for a function}~f(x_1,x_2,\dots,x_n),~\text{its tolerance} ~\delta_f = \sqrt{\sum_{i=1}^{n} {\left( \lfrac{\partial f}{\partial x_i} \delta x_i \right)}^2} \label{eqn:uncertainty-general-formula} \\
    \therefore \delta_{R_{total}} = \sqrt{{\left( \lfrac{\partial R_{total}}{\partial R} \delta_R \right)}^2} = \sqrt{{\left( \lfrac{1}{n} \delta_R \right)}^2} = \lfrac{1}{n} \delta_R \label{eqn:parallel-resistor-uncertainty}
\end{gather}
The $R_1$ resistors were made from 3 parallel resistors, each with tolerance $\pm1\%$ giving a total tolerance of $\pm0,\bar{3}\%$ and the calibration resistor was made from 4 parallel resistors with tolerance $\pm1\%$ giving a total tolerance of $\pm0,25\%$.

A last switch point was added to the circuit for the gold electrode's fringe guards, an example of which is shown in \reffig{fig:au-measurement-circuit}.
The voltage from $R_1$ was routed to a buffer op-amp with unity gain. 
Its output was then connected to the fringe guard, which effectively repeated the same voltage as the main pad while not affecting any measurements using them.
The other fringe guard could be switched to ground, allowing a current to be generated between the two. 
This current would ideally absorb any possible fringing from the main pads.
The same switch point also allowed the fringe guards to be electrically disconnected to test their effectiveness and to determine if they interfered with the measurement.
Lastly, as the fringe guards held the same voltage difference as the main pads and, in theory, had a higher resistance due to their smaller area, the current flowing between them was assumed to be less than that of the main pads; thus, there was no need to limit the current from the op-amp.

\begin{figure}[ht]
    \centering
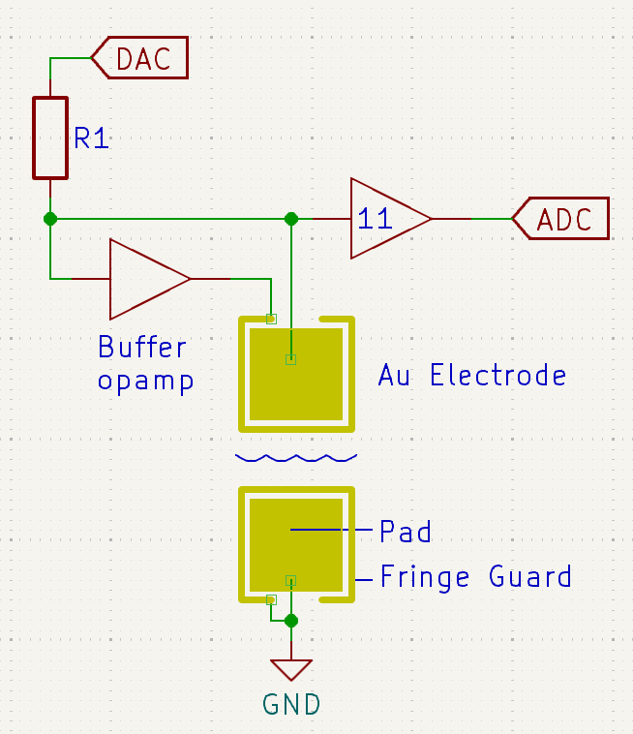
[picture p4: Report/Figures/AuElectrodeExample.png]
    
    \caption{A simplified representation of the resistance measurement circuit using the gold electrodes with the fringe guard.}
    \label{fig:au-measurement-circuit} %chktex 24
\end{figure}

\section{Salinity Calculation and Display}

In order to measure the salinity of the water, the probe \gls{pcb} would be lowered through the ice core hole into the water to capture salinity readings at various depths.
The measurements could either be captured automatically at preprogrammed depth or time intervals or triggered by the user using a controller.
The latter method was chosen for this project because it is a more user-friendly approach, allowing researchers to control precisely which depths the salinity measurements are made and giving them live updates about the probe's status and onboard sensors.

The controller was a straightforward \gls{pcb} with input buttons and rotary switches, two 7-segment displays, a \gls{rs485} communication port and a simple microcontroller.

Saltwater has a high \gls{emi}, which interferes with all wireless communication~\cite{pozzebon_near_field_communication_under_water_2015}.
While high-power wireless communication is viable for ranges up to $70m$, it is more reliable, cost-effective, and power efficient to use a wired connection~\cite{bergmann_wireless_underwater_data_transfer_2013}. 
\gls{rs485} is a robust, long-range embedded communication protocol that only requires a simple \gls{ic} to use, making it ideal for this project.
Additionally, the author was familiar with this protocol and had previous board-to-board communication experience with it.

\Gls{uart} to \gls{rs485} converters are common as most microcontrollers have a \gls{uart} communication port.
This project used half-duplex \gls{rs485} as it is the industry standard, and it is more cost-effective than full-duplex \gls{rs485}, which requires an additional \gls{uart} to \gls{rs485}.

The microcontroller was chosen from the STM32F030 series as it did not need to perform any complex calculations, and the author was familiar with this series.

With an external controller, a waterproofed probe could be lowered into the water to measure its salinity.
The chosen method of waterproofing the probe was to coat it with epoxy resin, as this was the most familiar and cost-efficient method available.
The other notable option is to create a waterproof housing for the probe, but this can be complex and expensive.
In addition to the circuitry shown in \reffig{fig:circuit-overview}, the probe had a temperature and depth sensor, which are discussed in \refsec{sec:temp-depth-measurement}, an \gls{rs485} communication port and a microcontroller.
The microcontroller was chosen from the STM32F4 series as it is the most cost-effective series with a \gls{fpu}, allowing the salinity to be calculated on board as per the equations in \refsec{sec:salinity-conductivity-relationship}.

\section{Temperature and Depth Measurement}\label{sec:temp-depth-measurement}

Waterproof depth sensors were too expensive for this project's budget, costing around $\$100$.
An alternative approach is to use a non-waterproof pressure sensor that is isolated from the water using a flexible membrane that allows the external pressure to be transmitted to the sensor.
The WF183DE pressure sensor was chosen as it was the most cost-effective sensor rated for above 50 meters of water pressure available at \texttt{JLCPCB}.
Should this approach fail, the backup plan was to use the controller to manually input a depth so that the salinity could still be calculated.

The temperature sensor was an arbitrarily chosen surface-mount sensor with high accuracy of $\pm 0,3\degree C$ and a wide temperature range of $-45$ to $130\degree C$.
Epoxy resin is a poor thermal conductor~\cite{epotek_thermally_conductive_epoxies}. 
Thus, the temperature sensor should be coated with a very thin layer of epoxy when the probe \gls{pcb} is cast, allowing for a more accurate measurement.
The choice of microcontroller and pressure sensor also provided this board with two alternative temperature sensors, which were less accurate but could be used in the event that the primary temperature sensor failed.

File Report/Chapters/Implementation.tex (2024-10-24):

% ----------------------------------------------------
% Implementation
% ----------------------------------------------------

\chapter{PCB Construction, Adjustments and Code}\label{ch:implementation}

\section{PCB Design}

The probe, controller and gold electrodes were fabricated on \glspl{pcb}, which were designed using KiCad software and manufactured with JLCPCB.
The KiCad design files can be found in the Git repository linked in \refappx{appx:gitrepo}. 
The gold electrodes were trivial, only requiring a single layer \gls{pcb} with simple pads and traces.

The probe \gls{pcb} was the most complex.
It was fabricated on a 4-layer \gls{pcb} with dimensions of $50\times 50mm$, shown in \reffig{fig:probe-pcb}.
JLCPCB offered a discount for 4-layer \glspl{pcb} that were smaller than $50\times 50mm$ in size.
While the probe should ideally be as small as possible to fit through the ice core, it was not designed to be smaller than $50\times 50mm$ to allow for a more straightforward debugging process.

%chktex-file 44
\begin{figure}[ht]
    \begin{minipage}{0.5\textwidth}
        \centering
        
    \end{minipage}
    \begin{minipage}{0.5\textwidth}
        \centering
        \begin{tabular}{cl} \hline
            1 & Programmer Port \\ \hline
            2 & Test Points \\ \hline
            3 & Pressure Sensor in a Protective Housing \\ \hline
            4 & $11\times$ Gain Op-Amp \\ \hline
            5 & Titanium Electrode Port \\ \hline
            6 & Gold Electrodes \\ \hline
            7 & Unity Gain Buffer Op-amp \\ \hline
            8 & \gls{dac} and Buffer Transistor \\ \hline
            9 & \gls{uart} to \gls{rs485} Converter \\ \hline
            10 & \gls{rs485} Port \\ \hline
            11 & \gls{uart} Port \\ \hline
            12 & STM32F4 Microcontroller \\ \hline
            13 & \glspl{led} \\ \hline
        \end{tabular}
    \end{minipage}
    \caption{The probe PCB with the gold electrodes attached and some adjustments made}
    \label{fig:probe-pcb} %chktex 24
    \textit{Note 1: The rest of the titanium electrode ports are behind the gold electrode.} \\
    \textit{Note 2: The other \glspl{ic} present are the TS3A4751 switches.}
\end{figure}

The probe was designed with the resistance measuring circuitry, the temperature and pressure sensors, the microcontroller, the \gls{uart} to \gls{rs485} converter and the \gls{rs485} port mentioned in \refch{ch:design}.
The gold and titanium electrode ports, which were placed at the bottom of the probe, were designed to allow them to be soldered perpendicular to it.
The other methods of attachment all presented a fundamental disadvantage: connecting them with wires added extra resistance, and attaching them parallel to the board or perpendicular facing downwards was considered too complex.

Several adjustments were made to facilitate easier debugging
A \gls{uart} port was added next to the \gls{rs485} port to allow for data to be streamed to a computer using a \gls{uart} to \gls{usb} converter.
Both ports also had reverse polarity protection added to prevent unintentional board damage. 
\glspl{led} were added next to the microcontroller, and a programmer port and test points were added at the top of the board to allow for visual feedback and circuit analysis.
With the programmer and communication ports at the top of the board and the electrodes at the bottom, the probe could safely be submerged while transferring its data to a laptop.

The controller \gls{pcb} was fabricated on a 2-layer board, which is shown in \reffig{fig:controller-pcb}, as the components were too large to fit on a $50\times 50mm$ 4-layer board.
JLCPCB offered a similar discount for 2-layer \glspl{pcb} that were less than $100\times 100mm$ in area.
Ultimately, the controller dimensions were $100\times 60mm$, which could comfortably fit all the components while taking advantage of \texttt{JLCPCB}'s discount.

\begin{figure}[ht]
    \begin{minipage}{0.5\textwidth}
        \centering
        
    \end{minipage}
        \begin{minipage}{0.5\textwidth}
            \centering
            \begin{tabular}{cl} \hline
            1 & Salinity 7-Segment Display \\ \hline
            2 & Depth 7-Segment Display \\ \hline
            3 & Rotary Switches \\ \hline
            4 & Power Input \\ \hline
            5 & \gls{uart} to \gls{rs485} Converter \\ \hline
            6 & \gls{rs485} Port \\ \hline
            7 & \gls{uart} Port \\ \hline
            8 & Input Buttons \\ \hline
            9 & Programmer Port \\ \hline
            10 & SD Card Port \\ \hline
            11 & STM32F0 Microcontroller \\ \hline
            12 & \glspl{led} \\ \hline
        \end{tabular}
    \end{minipage}
    \caption{The controller PCB with the rotary switch caps attached}
    \label{fig:controller-pcb} %chktex 24
\end{figure}

The controller was designed with the buttons, the rotary switches, the 7-segment displays, the \gls{uart} to \gls{rs485} converter, and the \gls{rs485} port mentioned in \refch{ch:design}.
The 7-segment displays were designated to display the salinity and depth of the water by default using silkscreen text, but they could be changed to display anything using software.
The components were placed user-friendly, allowing for easy use of the buttons and rotary switches.
Similarly to the probe, \glspl{led}, a \gls{uart} port and a programmer port were added to the board to allow for debugging of the board.
It should be noted that an SD Card Port was added for future development and testing but was not utilised during this project.

\section{PCB Adjustments}

Three adjustments were made to the probe \gls{pcb} to ensure it functioned as required, excluding the soldering of headers and the gold electrodes.
Firstly, one of the microcontroller's pins was unconnected to power and was corrected by soldering a wire between it and a pin with power, which can be seen on the left of the microcontroller.
Secondly, the footprint of the pressure sensor was horizontally reversed, which was corrected by flipping and soldering the depth sensor vertically.
A protective case was added around the pressure sensor to prevent it from being damaged during testing.
The casing would later function as the support for the waterproof membrane mentioned in \refsec{sec:temp-depth-measurement}.

Lastly, both op-amps were incorrectly chosen as they required a rail-to-rail voltage of $6V$ to operate, higher than the $3,3V$ provided.
Thus, they were replaced with an alternative op-amp model with the same footprint.
The temperature sensor also had an incorrect footprint, but this could not be rectified as it was discovered after the board was fabricated. 
Thus, the temperature sensor was not soldered to the board.
The pressure sensor's onboard temperature sensor was used instead.

The controller \gls{pcb} required no soldering adjustments.
There was a minor error in the pin assignments of the rotary switches, but this was corrected in the software and did not require any hardware changes.
Switch caps were 3D printed and attached to rotary switch shafts to make them easier to turn, making the controller more user-friendly.

\section{Probe Code}

The significant steps in measuring salinity are measuring the water's conductivity, temperature and pressure and then calculating its salinity.
An overview of this process is shown in \reffig{fig:probe-code-flowchart}.

\begin{figure}[ht]
    \centering
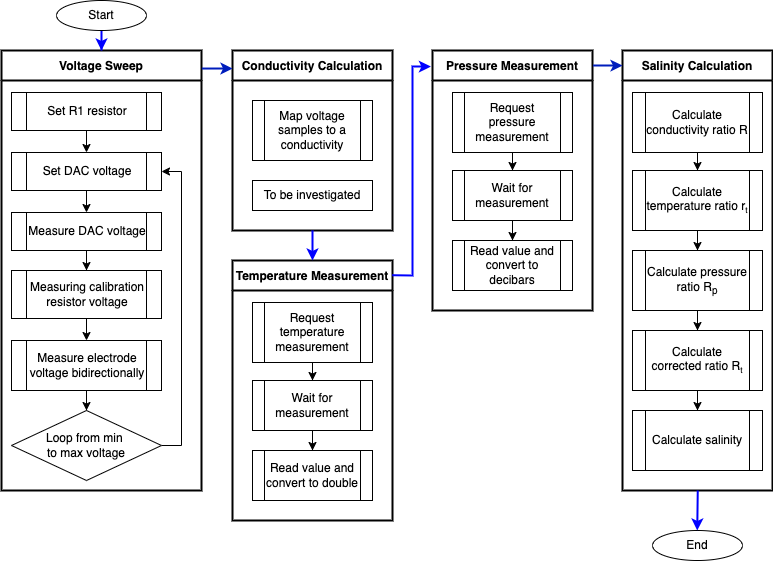
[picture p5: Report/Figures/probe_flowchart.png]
    
    \caption{The flowchart for the probe code that measures salinity.}
    \label{fig:probe-code-flowchart} %chktex 24
\end{figure}

The conductivity measurement was aimed at repeating the methodology that \refref{benjankar_ec_based_salt_measurement_2021} employed.
This requires a voltage sweep of the water sample, which is then mapped to a conductivity.
This devices specific mapping will have to be determined experimentally, as it is unique for different electrode sizes and materials.
The voltage sweep is achieved by incrementing the output of the \gls{dac} from a given start to end voltage.
At each step, the output of the \gls{dac} and the voltage drop across the calibration resistor and the electrodes are recorded.

To determine the resistance measuring accuracy, the resistance across the electrodes $R_E$ was calculated using the voltage drop across the electrodes and across the calibration resistor $R_C$, as shown in \refeqn{eqn:electrode-calib-resistance} to \refeqn{eqn:electrode-calib-resistance-final}.
The electrode resistances $R_E$ was calculated for each voltage sample and then averaged.

\begin{align}
 V_{ratio} &= \lfrac{V_{DAC}A_{11}A_{ADC}\lfrac{R_E}{R_1 + R_E}}{V_{DAC}A_{11}A_{ADC}\lfrac{R_C}{R_1 + R_C}} = \lfrac{\lfrac{R_E}{R_1 + R_E}}{\lfrac{R_C}{R_1 + R_C}} \label{eqn:electrode-calib-resistance} \\
 \lfrac{R_E}{R_1 + R_E} &= V_{ratio} \lfrac{R_C}{R_1 + R_C} \rightarrow k \label{eqn:electrode-calib-resistance-simplified} \\
 R_E &= \lfrac{kR_1}{1 - k} \label{eqn:electrode-calib-resistance-final}
\end{align}

This method of calculating resistance using a voltage ratio with a known resistance allows the probe to nullify all scalar inaccuracies in the circuit, including the \gls{dac}, \gls{adc} and op-amp gain error, as they will be present in both voltage measurements.
However, this method is still vulnerable to offset inaccuracies, including \gls{dac} and \gls{adc} offset errors, op-amp input offset and input bias currents, the $R_1$ resistance errors and the resistance added by the switches and traces.

As previously mentioned, the pressure and temperature measurements are taken from the WF183DE pressure sensor.
This sensor operates similarly for both measurements: a request is made to make a measure, it can then be polled until the measurement is ready, and then the measurement can be read.

Once the conductivity, temperature and pressure measurements are taken and converted into the required units of $Sm^{-1}$, $\degree C$ and $dbar$ respectively, salinity can be calculated as shown in \refsec{sec:salinity-conductivity-relationship}.
Additionally, if requested, any of the temperature, depth, resistance, or conductivity measurements can be calculated individually and transmitted to the controller.

\section{Controller Code}

The controller's primary function for the prospective user was to instruct the probe to take a measurement and display it. However, the controller was given additional functionality for testing and investigation purposes, which allowed the controller to update the probe's configuration.

The common-cathode 7-segment displays displayed the various measurements from the probe.
The displays' digits were individually written to by writing the digit code and keeping the corresponding digit's cathode low while keeping the others high.
A timer controlled \gls{dma} was used to write to each digit in quick succession, giving the illusion of all the digits being on simultaneously.

The leftmost rotary switch was used to navigate the menu, which consisted of the default showing both salinity and depth, individual measurements of temperature, depth, resistance, conductivity, and salinity, and the probe's configurable parameters.
The menu names were displayed on the top 7-segment display, and the selected menu item was displayed on the other.
This created some limitations on what could be displayed. 
For instance, the best display of the word `temperature' was `teP', but all menu items had a unique, relatively clear name.

When the user selected a measurement menu item, the top switch was configured to request that measurement from the probe and display it; when the user selected a configuration menu item, the top switch was configured to update the probe's configuration.
The other two rotary switches adjusted the probe's configurable parameters, further discussed in \refsec{sec:board-to-board-communication}.
The bottom switch was configured to reset the probe and the controller should an error occur.

\section{Board-to-Board Communication}\label{sec:board-to-board-communication}

The probe and controller communicate using half-duplex \gls{rs485}, which is converted on both sides to \gls{uart}.
This makes the protocol effectively half-duplex \gls{uart} communication from the perspective of the microcontrollers.
The probe was configured to be in receive mode, where it would perpetually wait for a one-byte command from the controller.
All the possible commands and expected transactions are shown in \reffig{fig:rs485-flowchart}.

\begin{figure}[ht]
    \centering
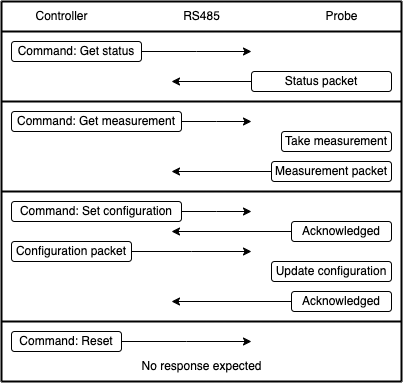
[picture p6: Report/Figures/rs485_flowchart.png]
    
    \caption{The flowchart for the board-to-board communication protocol denoting the four transaction types. The arrows denote the direction of the packets being sent over the \gls{rs485} link.}
    \label{fig:rs485-flowchart} %chktex 24
\end{figure}

While not directly available to the user, the controller could request a status byte to which the probe would respond with \textit{idle}, \textit{busy} or \textit{error} depending on its state.
This allowed for some simple error checking and communication flow, which could be integrated into more robust error handling in the future.
When the user requests a measurement, the controller sends the corresponding request command, to which the probe will respond with the measurement data.
The data was returned as a 3-byte, fixed-point float.

When the user requested a configuration update, the controller transferred a configuration packet using the expected transaction.
Once the probe was entirely cast in epoxy resin, the configuration could only be updated this way, so all possibly useful, configurable parameters are included.
This included which electrode to use (including whether to use the fringe shield), the $R_1$ resistor to use, the directionality of the resistance measurement (unidirectional or bidirectional), the voltage sweep start, end and number of steps, among other parameters.
Some parameters, such as the directionality, were unlikely to be changed from their default value (bidirectional) but were included to cover any unforeseen circumstances.

When the user resets the boards using the controller's bottom switch, a reset command was sent to the probe before the controller reset itself.
This command allows for resetting the probe should a system error occur.
However, this only works provided the \gls{rs485} link is still operational.
Otherwise, the entire system must be powered off and on again to reset the probe.
The reset on both microcontrollers is triggered using software to set the \gls{sys_reset_req} bit in the \gls{scb} register, which triggers a system reset similar to pulling the reset pin low.

\section{Probe Epoxy Casting}\label{sec:probe-epoxy-casting}

The circuitry on the probe had to be protected from the salt water while the electrodes were submerged, which was achieved using \textit{Kristal 20} epoxy resin.
Before casting the epoxy, the \gls{rs485} ports on the controller and probe were connected using a multicore cable, which connected their power, ground and the \gls{rs485} data lines, which can be seen in \reffig{fig:epoxy-top}.
A casting mould was created using acrylic sheets, which are commonly used for epoxy moulds as they tend not to stick to the epoxy.
The sheets were cut and secured using hot glue, as seen in \reffig{fig:epoxy-side}.

\begin{figure}[ht]
    \begin{minipage}{0.49\textwidth}
        \centering
        
        \caption{A top view of the probe casting mould, the controller and the connecting cable.}
        \label{fig:epoxy-top} %chktex 24
    \end{minipage}
    \begin{minipage}{0.49\textwidth}
        \centering
        
        \caption{A side view of the probe casting mould showing the gold electrode spacers.}
        \label{fig:epoxy-side} %chktex 24
    \end{minipage}
\end{figure}

The gold electrodes were precisely spaced using 3D-printed spacers, which were attached during the casting process and removed once the epoxy had cured.
Lastly, two areas of the probe still needed to be accessed: the programmer and \gls{uart} ports and the titanium electrode ports.
This would simplify further testing and allow the titanium electrodes to be optimally spaced through experimentation instead of estimations.
These areas were isolated using \textit{Prestick}, a rubber-based reusable putty adhesive. 
The adhesive was removed after the epoxy had cured, allowing access to the aforementioned areas.

The probe was removed from the mould after the epoxy had cured, shown in \reffig{fig:probe-final}.
The \textit{Prestick} adhesive was relatively easy to remove, and the desired areas were still accessible, allowing the titanium electrode to be added.
Titanium is challenging to solder, requiring a complex process and advanced machinery that was not available for this project~\cite{totalmateria_joining_titanium_2005}.
Instead, thin copper wire was tightly wrapped around the last $5mm$ of the titanium electrode, which was folded over to secure the copper wire, as shown in \reffig{fig:titanium-electrodes}.
This configuration made connecting the electrodes to their ports easy using standard soldering and provided a continuous connection between the probe and the titanium electrode.

\begin{figure}[ht]
    \begin{minipage}{0.5\textwidth}
        \centering
        
        \caption{The probe after the epoxy casting process with the titanium electrodes and pressure sensor's flexible membrane attached.}
        \label{fig:probe-final} %chktex 24
    \end{minipage}
    \begin{minipage}{0.5\textwidth}
        \centering
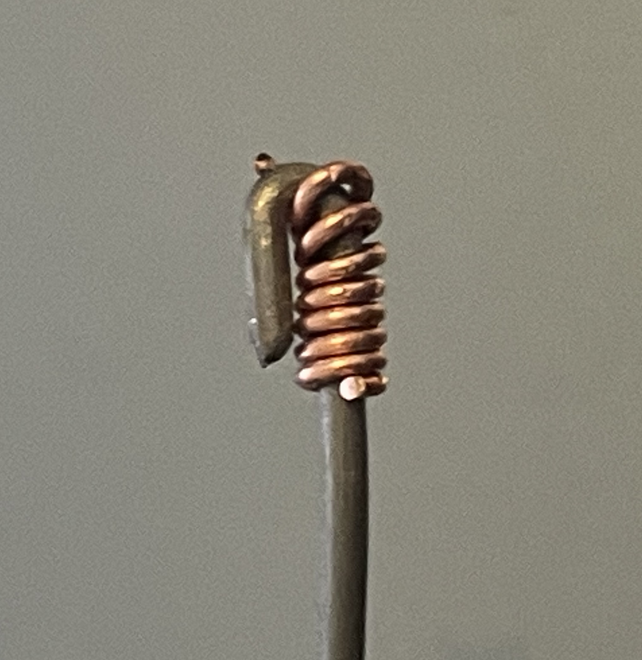
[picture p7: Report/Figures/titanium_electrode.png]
        
        \caption{A close-up of the titanium electrode with the copper wire attached.}
        \label{fig:titanium-electrodes} %chktex 24
    \end{minipage}
\end{figure}

The unevenness of the mould and the hot glue created some rough edges along the epoxy.
These could be laser cut to a smooth finish for the final product, but this was considered unnecessary for the experiments conducted in this project.

Lastly, hot glue was used to attach a flexible membrane to the pressure sensor's protective casing.
The membrane was taken from the packaging of the gold electrode \glspl{pcb} as it was readily accessible and had the required flexibility and durability to prove the concept.
The final device would require further investigation into a more suitable material.
The protective casing was also coated in a thin layer of hot glue as the 3D printing process used to create it had a small probability of being porous.

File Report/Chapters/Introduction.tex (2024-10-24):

% ----------------------------------------------------
% Introduction
% ----------------------------------------------------

\chapter{Introduction}\label{ch:introduction}

\section{Problem Statement}

There are several methods and designs for measuring salinity which is commonly understood as the salt content of water.
However, Antarctica's freezing temperatures and harsh conditions make it challenging for scientists to study this metric there.
The current method of measuring involves capturing a water sample from the ocean beneath the ice sheet and bringing it to the surface for measurement.
This process alters some water's physical properties, such as temperature and pressure, which can affect the salinity measurement.
This project aims to design a device that can more accurately measure the salinity by using a probe to take measurements at various depths in the ocean.

\section{Background}

Antarctica is covered in a vast sheet of ice consisting of around 30 million cubic kilometres in volume, which is about 60\% of the world's fresh water~\cite{NSIDC_ice_sheet_facts_2024}.
Part of the ice sheets rests on land, known as the continental ice sheet, while the rest floats on the ocean, known as the ice shelves~\cite{nsidc_ice_shelves_2024}.
The ice sheet supports a variety of species both above and below it, as well as an ecosystem within the ice itself~\cite{noaa_arctic_expedition_2002}.

The ice shelves surrounding the Antarctic continent constantly wax and wane~\cite{nasa_antarctic_sea_ice_2021}, with the ice thickening during winter with water and salt accumulating from precipitation, sea spray, and ocean water freezing in direct contact with the ice~\cite{hogg_extending_record_ice_shelf_thickness_2021}.
When the water freezes, the salts are expelled from the mixture,  creating small pockets and highly saline water channels known as brine channels.
The brine channels form a habitat for several microorganisms that have adapted to the cold, harsh environment and a new habitat when they drain into the ocean below.
Frigid brine and regular seawater mix beneath the ice shelves, creating a mixing zone which forms a unique environment that supports life.
Scientists working with the \gls{uct} are currently investigating the properties of the mixing zone, such as the water's salinity, temperature, currents, light penetration, and more.

To measure any given property, an ice core is drilled through the ice shelf down to the water's surface, and two main methods are employed to measure the brine-sea water mixture.
Either a probe is lowered into the water through the ice core hole, allowing measurements to be taken at multiple depths, or a sample of the water is captured by lowering an open canister known as a Niskin bottle into the water, closing it at the desired depth, and retrieving it for analysis with hand-held instruments.
Salinity is currently being measured using the latter method, which could be improved as the water sample changes temperature and pressure as it is brought to the surface, which can affect the salinity measurement.

\section{Objectives}

The objectives of this project are to design and develop a prototype device for measuring the salinity of the water beneath the ice shelf.
The prototype should aid in investigating its feasibility and understanding the methodology for measuring salinity.
It should set the foundation for a future device to be developed that can be used in the field.
The final device should be able to withstand Antarctica's harsh temperatures and conditions, but these will only be secondary considerations in this project.

% \section{System Requirements}
% \lipsum[1]

\section{Scope \& Limitations}

This project's scope includes the design and development of a prototype device for measuring salinity.
This includes researching the relevant literature that details devices with similar functionality, the theory behind measuring salinity, followed by the design and development of a prototype device that can test the properties of salt water and lead to a method of measuring salinity.
The prototype development involves testing and evaluating the device to determine its effectiveness in measuring salinity.
Additionally, this project should aim to develop the prototype as a separate probe and control unit.
The scope does not extend to any development for the final device beyond the prototype nor the analysis of any data captured should the prototype be used in the field.

This project has a budget limitation of R2000 for the entire design, development and testing.
This budget can only be spent through \gls{uct} with their approved suppliers and vendors.
The project must be completed in 14 weeks from the start to the submission of the final report.

\section{Report Outline}

Following this introduction in \refch{ch:introduction}, the literature review in \refch{ch:literature} will give an overview of salinity, the methods of measuring it, and the devices used to measure it.
The method of calculating salinity is cover in \refch{ch:theory-development}.
This is followed by the design of the probe circuitry, its electrodes and a controller required to measure salinity and a controller  in \refch{ch:design}.
\refch{ch:implementation} details the fabrication of the designed probe circuitry and the controller onto \glspl{pcb}, the correction made to them, and the waterproofing of the probe by casting it into epoxy.
\refch{ch:testing} details the evaluation of the probe's resistance measurement accuracy, following by an investigation into and evolution of a method to measure conductivity and to calculate salinity.
Finally, \refch{ch:conclusions} concludes the report with a summary of the project's objectives, the results obtained, and \refch{ch:recommendations} provides recommendations for future work.

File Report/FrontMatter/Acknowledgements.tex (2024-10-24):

\chapter*{Acknowledgements}

% Financial

% Academic
I would like to thank my supervisor, Justin Pead, for his guidance and support throughout the project. 
He provided valuable insight into the design and testing of the prototype, and assistance with the writing of this report.
I would also like to thank Brendon Daniels for his delicate soldering and adjustments made to the prototype

% Friends
I would like to thank my engineering friends, Si Teng Wu, Deereshan Naidoo, Kian Frassek, and Robert Dugmore for their assistance with the design and debugging of the prototype and the writing of this report.

% Family
Lastly, I would like to thank my family for their support extensive throughout my studies.

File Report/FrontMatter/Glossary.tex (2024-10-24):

\makenoidxglossaries

\newacronym{uct}{UCT}{University of Cape Town}
\newacronym{psu}{PSU}{Practical Salinity Units}
\newacronym{ppt}{$\text{\textperthousand}$}{Parts Per Thousand}
\newacronym[shortplural=CTDs]{ctd}{CTD}{Conductivity, Temperature, Depth} 
\newacronym[shortplural=PCBs, longplural=Printed Circuit Boards]{pcb}{PCB}{Printed Circuit Board}
\newacronym{enig}{ENIG}{Electroless Nickel Immersion Gold}
\newacronym[shortplural=DACs, longplural=Digital to Analogue Converters]{dac}{DAC}{Digital to Analogue Converter}
\newacronym{adc}{ADC}{Analogue to Digital Converter}
\newacronym{emi}{EMI}{Electromagnetic Interference}
\newacronym{fpu}{FPU}{Floating Point Unit}
\newacronym{sst}{SST}{Sea Surface Temperature}
\newacronym{ppm}{ppm}{parts per million}
\newacronym{uart}{UART}{Universal Asynchronous Receiver-Transmitter}
\newacronym[shortplural=LEDs, longplural=Light Emitting Diodes]{led}{LED}{Light Emitting Diode}
\newacronym{dma}{DMA}{Direct Memory Access}
\newacronym{sys_reset_req}{SYSRESETREQ}{System Reset Request}
\newacronym{scb}{SCB}{System Control Block}
\newacronym[shortplural=ICs, longplural=Integrated Circuits]{ic}{IC}{Integrated Circuit}
\newacronym{rs485}{RS-485}{Recommended Standard \#485}
\newacronym{usb}{USB}{Universal Serial Bus}
\newacronym{lcr}{LCR}{Inductance (L), Capacitance (C), Resistance (R)}
\newacronym{ac}{AC}{Alternating Current}
\newacronym{dc}{DC}{Direct Current}
\newacronym{lcd}{LCD}{Liquid Crystal Display}

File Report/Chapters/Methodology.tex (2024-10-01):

% ----------------------------------------------------
% Methodology
% ----------------------------------------------------

\chapter{Methodology}\label{ch:methodology}

\section{Device Design}

\subsection{Salinity Measurement Method}

\textit{help}
Of the available methods for measuring salinity, the most common method used in oceanography is the conductivity method.
This is because conductivity of salt water is the easiest to repeatably measure and provides the most consistent accuracy.
Information on other methods can be found in the literature review.

One of the most common methods of measuring conductivity of a liquid is to measure the resistance between two electrodes or probes in the liquid and use that to determine its conductivity.
The shape and material of the probes are an important factor which affect the measurement accuracy and drift as well as the ease of calculation from resistance to conductivity.

\subsection{Conductivity Probe Material}

Ideal probes for measuring conductivity in salt water need to have zero resistance, infinite corrosion resistance and be able to confine the electrical current in the water to a specific volume.
The zero resistance will allow the resistance that it measured to be entirely due to the water, although most conductive materials have a conductivity in the order of $10^8 S/m$ which causes negligible resistance compared to water which has a conductivity range of $0-5 S/m$. %https://atlas-scientific.com/blog/water-conductivity-range/ https://byjus.com/physics/conductivity-of-water/#:~:text=Viscosity%20And%20Density-,Salt%20Water%20Conductivity,and%20chlorine%20ions%20(NaCl).
The infinite corrosion resistance will allow the probes to last indefinitely in the highly corrosive salt water.
The confinement of the electrical current allows for an easier calculation of the conductivity $\rho$ from resistance $R$ if the cross-sectional area $A$ and length $l$ of the water between the probes is known as shown by \refeqn{eqn:conductivity-from-resistance}.
\begin{equation}
    \rho = \lfrac{RA}{l}
    \label{eqn:conductivity-from-resistance}
\end{equation}
There are several metals known for their corrosion resistance which are used in corrosive environments including marine environments.
The most abundant of these are aluminium and stainless steel, followed by nickel and copper alloys, such as Monel or brass, and finally titanium.
Additionally, the precious metals gold, silver and platinum are also known for their exceptional corrosion resistance which exceeds the aforementioned metals, although they are significantly more expensive.

The choice of material aimed at using materials with the highest corrosion resistance while still choosing materials that were attainable and within this project's budget.
Titanium is the most corrosive resistant of the non-precious metals and has an acceptable resistivity of $4.5\e{-7}\Omega\cdot m$ which is about 25 times that of copper.
Titanium wire was available through off-cuts from a project being conducted by the Chemical Engineering Department of the University of Cape Town, and thus it was possible to use this material for the electrodes.

Of the precious metals, gold is one of the most accessible as it is a common material used in \glspl{pcb} manufacturing primarily because of its high corrosion resistance while it maintains a low resistivity of $2.44\e{-8}\Omega\cdot m$ similar to copper.
\gls{enig} \gls{pcb} manufacturing is a process where nickel followed by gold are deposited onto the copper of the \gls{pcb} using chemical reactions.
While this process is expensive, it is affordable within this project's budget and made gold a possible material for the electrodes.

Gold and titanium were both used as electrodes for this project due to their high corrosion resistance, conductivity and availability.

\subsection{Conductivity Probe Design}

Gold electrodes made using the \gls{enig} \gls{pcb} manufacturing process were chosen to be the primary electrodes for the device.
The high corrosion resistance and conductivity of gold were advantageous, and the \gls{pcb} allowed the probes to be made with a known area and length of the water between the probes.

Some scientific papers that attempt to measure salinity have an uncertainty on whether salt water has a constant resistivity relative to the voltage applied to it or not.
In order to verify this, the resistance of the water between the probes needed to be measured at different voltages while other factors were kept constant which necessitated close attention to the fringing effect of the electrical current between the probes.
Thus, wide flat pads were used on the \gls{pcb} probes, and they were placed them close together to reduce the amount of current fringing allowing for a more accurate calculation of the conductivity.
To further reduce the fringing, a fringe guard was added to the probes which consisted of a pad that outlined the main conductivity pads that repeated the same voltage as the main pads using an op-amp which would allow for the fringing to be taken up by the fringe guard and not affect the resistance measurement.

The dimensions of the gold electrodes were chosen somewhat arbitrarily with the pads having a large area while being placed relatively close together to reduce the fringing but not too close to prevent water from flowing between the pads.
Additionally, the aim was to keep the resistance between the pads low to lower the amount of voltage required to generate a current through the water thus further reducing the fringing. 
The gold electrodes were designed with a $20mm \times 20mm$ pad area with a $2mm$ wide fringe guard surrounding the majority of the pad and were spaced $10mm$ apart as shown in \reffig{fig:gold-electrode}.
This gave a resistance of $3.75\Omega$ to $6.25\Omega$ between the gold electrodes for salinities of $40$ to $25$ on the practical salinity scale respectively.
\begin{figure}
    \centering
    
    \caption{The gold electrode \gls{pcb} design.}
    \label{fig:gold-electrode} %chktex 24
\end{figure}

The titanium electrodes are substantially simpler and cheaper than the gold electrodes and would be the preferred electrodes if the fringing effect could be accounted for.
Provided the testing with the gold electrodes is able to prove a constant resistance-voltage relationship, the fringing effect between the titanium electrodes could be measured and accounted for allowing for them to be used as the primary electrodes in a future iteration of the device.
The titanium wire that was available for this project was $1mm$ in diameter and in order to account for the unknown resistance between the electrodes, the design allowed for an adjustable spacing between the electrodes and adjustable electrode length.

\subsection{Resistance Measurement Method}

The most common and practical method of measuring resistance is to use a resistor divider circuit.
Current meters are also used to measure resistance, but most of them use the same principle of a resistor divider circuit to determine the current.
This project chose to use a large $R_1$ in series with the electrodes such that the voltage between the probes would be lower which would further reduce the fringing effect.
The measurement taken from the voltage divider was then amplified by a factor of 11 to increase the resolution of the measurement.

\subsection{Circuit Overview}
\textit{additional advantage : will never short circuit}
\begin{figure}
    \centering
    
    \caption{A simplified representation of the resistance measuring circuit.}
    \label{fig:circuit-overview} %chktex 24
\end{figure}

\reffig{fig:circuit-overview} shows a simplified overview of the resistance measuring circuit that was used in this project.
The voltage driving the resistor divider was provided by a \gls{dac} such that the voltage could be varied and the resistance-voltage relationship could be determined for the titanium electrodes.
The resistance across the titanium electrodes remained uncertain and thus, in addition to the varied spacing and electrode length, alternative resistor values for $R_1$ were provided which could be selected using solder jumpers on the device.

The $R_1$ values were chosen to be $100\Omega$, $1k\Omega$ and $10k\Omega$ which would be used when the resistance between the probes is $1\Omega - 10\Omega$, $10\Omega - 100\Omega$ and $100\Omega - 1k\Omega$ respectively.
This would allow for a minimum resolution of $11\%$ of $V_{CC}$ for the voltage measurement by the \gls{adc} as shown by \refeqn{eqn:adc-resolution}.
\begin{equation}\label{eqn:adc-resolution}
    \lfrac{1\Omega}{1\Omega + 100\Omega} * 11 = 11\%
    \lfrac{10\Omega}{10\Omega + 100\Omega} * 11 = 100\%
\end{equation} 

Switch 1 allows $R_1$ to be connected to any of the four electrodes or a calibration resistor of $5\Omega$ and switch 2 allows for the other electrode to be connected to ground.
For example, switch 1 could be connected to Ti+ and switch 2 could be connected to Ti- to measure the resistance between the titanium electrodes.
This configuration also allows current to flow in both directions between electrodes which can prevent excessive build of chlorine gas or sodium electroplating on the electrodes by taking a resistance measurement in both directions in rapid succession.

In order to increase the measurement accuracy of the resistance, multiple high accuracy resistors were placed in series to attain the values of $R_1$ and the calibration resistor as this decreases the uncertainty of their resistance.
This decreases the total uncertainty $\delta_{R_{total}}$ by a factor of the number of parallel resistors $n$ compared to the individual resistor uncertainty $\delta_R$ as shown by \refeqn{eqn:parallel-resistor-total} to \refeqn{eqn:parallel-resistor-uncertainty}.
\begin{equation}[!h]\label{eqn:parallel-resistor-total}
    R_{total} = {\left[ \sum_{i=1}^{n} \lfrac{1}{R} \right]}^{-1} = {\left(\lfrac{n}{R}\right)}^{-1} = \lfrac{1}{n}\cdot R
\end{equation}
\begin{equation}[!h]\label{eqn:uncertainty-general-formula}
    \text{for a function}~f(x_1,x_2,\dots,x_n), \text{its uncertainty} ~\delta_f = \sqrt{\sum_{i=1}^{n} {\left( \lfrac{\partial f}{\partial x_i} \delta x_i \right)}^2}
\end{equation}
\begin{equation}[!h]\label{eqn:parallel-resistor-uncertainty}
    \therefore \delta_{R_{total}} = \sqrt{{\left( \lfrac{\partial R_{total}}{\partial R} \delta_R \right)}^2} = \sqrt{{\left( \lfrac{1}{n} \delta_R \right)}^2} = \lfrac{1}{n} \delta_R
\end{equation}
The resistances for $R_1$ were made from 3 parallel resistors with tolerance $\pm1\%$ giving a total uncertainty of $\pm0.\bar{3}\%$ and the calibration resistor was made from 4 parallel resistors with tolerance $\pm1\%$ giving a total uncertainty of $\pm0.25\%$.

\begin{figure}[!h]
    \centering
    
    \caption{A simplified representation of the resistance measurement circuit using the gold electrodes with the fringe guard.}
    \label{fig:au-measurement-circuit} %chktex 24
\end{figure}

\reffig{fig:au-measurement-circuit} shows an example switch configuration where the gold electrodes are used.
The buffer op-amp has unity gain and is used to repeat the voltage going to the pad of the top electrode to its fringe guard while the other pad and fringe guard are connected to ground.
In theory, this should allow for the fringing to be absorbed by the fringe guard and not affect the resistance measurement, however switches were added electrically connect or disconnect the fringe guard should it interfere with the resistance measurement.
The current flowing between the fringe guards was assumed to be less than that of the pads and thus there was no need to limit the current from the op-amp.

\subsection{Salinity Calculation and Display}

In order to measure the salinity of the sea ice, the probe needed to be lowered into the water and measure salinity at various depths.
There are two methods for capturing the salinity data: either to constantly record the salinity data as the device it lowered through the water column or to have the device take a measurement when instructed by a controller.
The former method creates logistical problems with waterproofing the device and retrieving data while the latter was a more user-friendly approach allowing researchers to control exactly which depths the salinity is measured at and was chosen for this project.

The controller consisted of a \gls{pcb} with input buttons and two output 7-segment displays to control and relay salinity information, and a RS485 communication port and a simple microcontroller.
The RS485 communication port was chosen as the communication protocol as RS485 has the longest range and a high noise resistance which is necessary for the device to be used in the ocean which has high \gls{emi}.
The microcontroller was arbitrarily chosen from the STM32F030 series as it was relatively cheap, and it did not need to perform any complex calculations.
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

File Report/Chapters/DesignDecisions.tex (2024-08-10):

% ----------------------------------------------------
% Design Decisions
% ----------------------------------------------------
\chapter{Design Decisions} \label{ch:designdecisions}
% ----------------------------------------------------
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

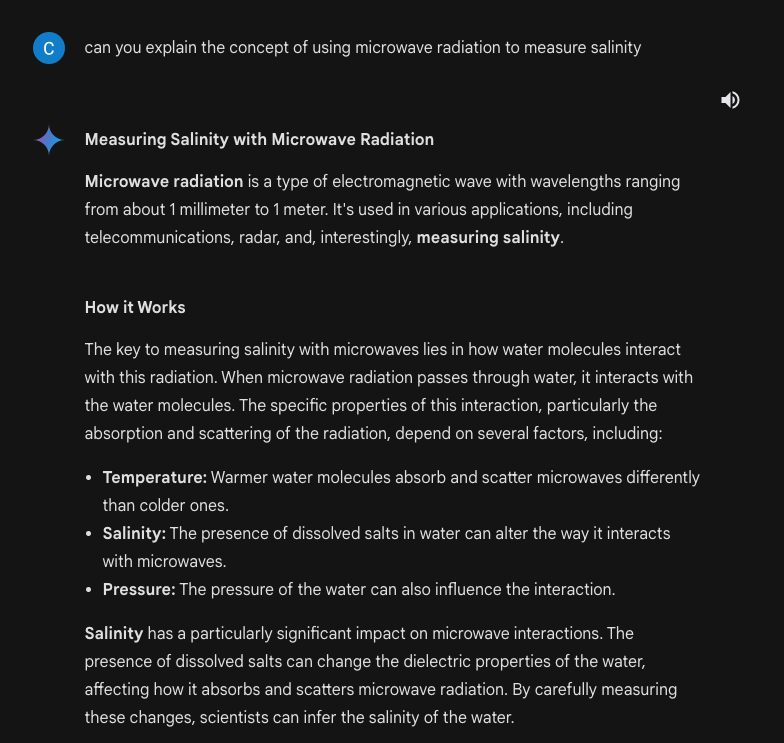
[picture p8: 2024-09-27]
Report/Figures/AI_Use/concept_overviews.png

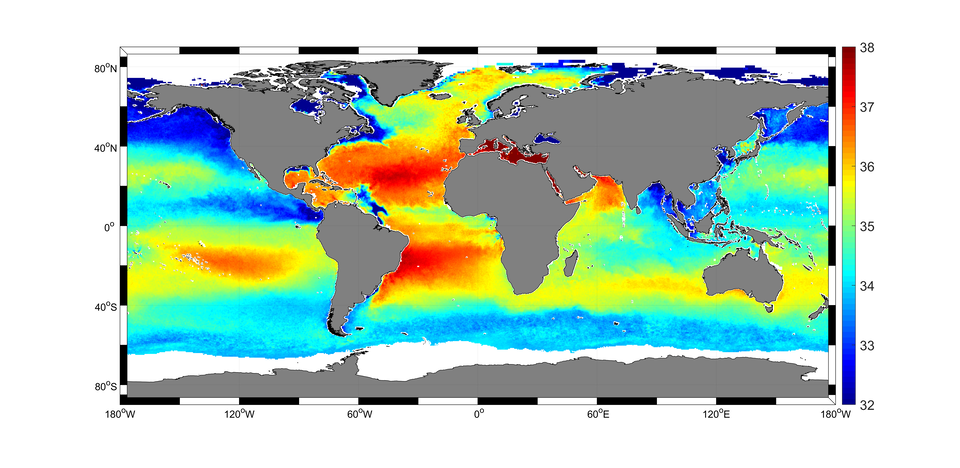
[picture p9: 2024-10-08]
Report/Figures/salinity_distribution.png

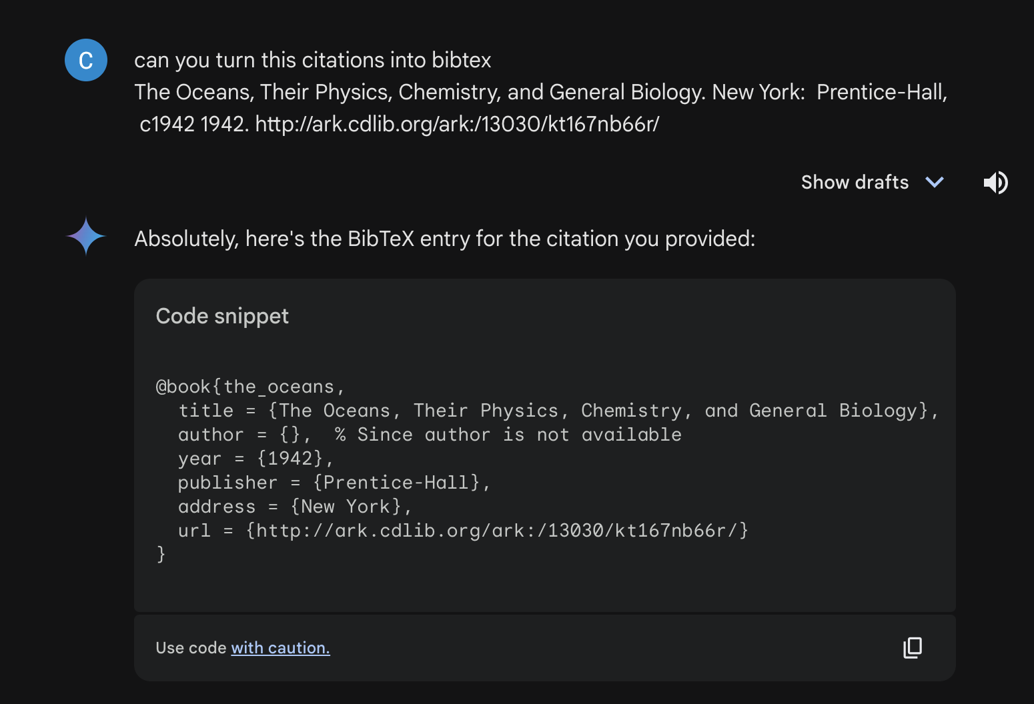
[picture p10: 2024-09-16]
Report/Figures/AI_Use/bibtex_citing.png

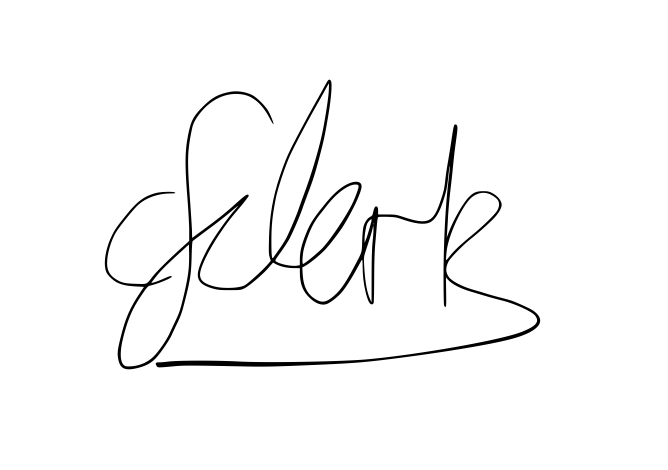
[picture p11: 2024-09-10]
Report/Figures/Signature.png

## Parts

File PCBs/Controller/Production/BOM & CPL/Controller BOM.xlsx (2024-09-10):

Comment | Designator | Footprint | JLCPCB Part#
100n | C1 | Capacitor_SMD:C_0603_1608Metric | C14663
100n | C2 | Capacitor_SMD:C_0603_1608Metric | C14663
4.7u | C4 | Capacitor_SMD:C_0603_1608Metric | C69182
10n | C5 | Capacitor_SMD:C_0603_1608Metric | C57112
1u | C6 | Capacitor_SMD:C_0603_1608Metric | C15849
GREEN | D1 | LED_SMD:LED_0805_2012Metric | C2297
RED | D2 | LED_SMD:LED_0603_1608Metric | C2286
Micro_SD_Card_Det1 | J2 | 4022S:microSDcard | C393941
10k | R1 | Resistor_SMD:R_0603_1608Metric | C25804
10k | R3 | Resistor_SMD:R_0603_1608Metric | C25804
10k | R4 | Resistor_SMD:R_0603_1608Metric | C25804
1k | R5 | Resistor_SMD:R_0603_1608Metric | C21190
10k | R8 | Resistor_SMD:R_0603_1608Metric | C25804
1k | R9 | Resistor_SMD:R_0603_1608Metric | C21190
10k | R10 | Resistor_SMD:R_0603_1608Metric | C25804
10k | R11 | Resistor_SMD:R_0603_1608Metric | C25804
10k | R12 | Resistor_SMD:R_0603_1608Metric | C25804
10k | R13 | Resistor_SMD:R_0603_1608Metric | C25804
120 | R14 | Resistor_SMD:R_0603_1608Metric | C22787
300 | R15 | Resistor_SMD:R_1206_3216Metric | C17887
300 | R16 | Resistor_SMD:R_1206_3216Metric | C17887
300 | R17 | Resistor_SMD:R_1206_3216Metric | C17887
300 | R18 | Resistor_SMD:R_1206_3216Metric | C17887
300 | R19 | Resistor_SMD:R_1206_3216Metric | C17887
300 | R20 | Resistor_SMD:R_1206_3216Metric | C17887
Switch | SW1 | 4022S:Push_Button_SPDT | C318884
Switch | SW2 | 4022S:Push_Button_SPDT | C318884
STM32F030R8Tx | U1 | Package_QFP:LQFP-64_10x10mm_P0.5mm | C39105
Salinity | U3 | 4022S:SP20561 | C98928
Depth | U4 | 4022S:SP20561 | C98928
SP3485EN | U8 | Package_SO:SOIC-8_3.9x4.9mm_P1.27mm | C8963

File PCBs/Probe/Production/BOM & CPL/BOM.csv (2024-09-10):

Reference | Value | Datasheet | Footprint | Qty | JLC Part no. | Extended | Cost
C1 | 2.2u | ~ | Capacitor_SMD:C_0603_1608Metric | 1 | C23630 | False | 0,0055
C2 | 100n | ~ | Capacitor_SMD:C_0603_1608Metric | 1 | C14663 | False | 0,0021
C3 | 2.2u | ~ | Capacitor_SMD:C_0603_1608Metric | 1 | C23630 | False | 0,0055
C4 | 10u | ~ | Capacitor_SMD:C_0603_1608Metric | 1 | C19702 | False | 0,0048
C5 | 1u | ~ | Capacitor_SMD:C_0603_1608Metric | 1 | C15849 | False | 0,0043
C6 | 4.7u | ~ | Capacitor_SMD:C_0603_1608Metric | 1 | C69182 | False | 0,0055
C7 | 100n | ~ | Capacitor_SMD:C_0603_1608Metric | 1 | C14663 | False | 0,0021
C8 | 100n | ~ | Capacitor_SMD:C_0603_1608Metric | 1 | C14663 | False | 0,0021
C9 | 4.7u | ~ | Capacitor_SMD:C_0603_1608Metric | 1 | C69182 | False | 0,0055
C10 | 100n | ~ | Capacitor_SMD:C_0603_1608Metric | 1 | C14663 | False | 0,0021
C11 | 100n | ~ | Capacitor_SMD:C_0603_1608Metric | 1 | C14663 | False | 0,0021
C12 | 100n | ~ | Capacitor_SMD:C_0603_1608Metric | 1 | C14663 | False | 0,0021
C13 | 100n | ~ | Capacitor_SMD:C_0603_1608Metric | 1 | C14663 | False | 0,0021
C14 | 100n | ~ | Capacitor_SMD:C_0603_1608Metric | 1 | C14663 | False | 0,0021
C15 | 100n | ~ | Capacitor_SMD:C_0603_1608Metric | 1 | C14663 | False | 0,0021
C16 | 100n | ~ | Capacitor_SMD:C_0603_1608Metric | 1 | C14663 | False | 0,0021
C17 | 10n | ~ | Capacitor_SMD:C_0402_1005Metric | 1 | C15195 | False | 0,0012
C18 | 10n | ~ | Capacitor_SMD:C_0402_1005Metric | 1 | C15195 | False | 0,0012
C19 | 10n | ~ | Capacitor_SMD:C_0402_1005Metric | 1 | C15195 | False | 0,0012
C20 | 10n | ~ | Capacitor_SMD:C_0402_1005Metric | 1 | C15195 | False | 0,0012
C21 | 10n | ~ | Capacitor_SMD:C_0402_1005Metric | 1 | C15195 | False | 0,0012
C22 | 10u | ~ | Capacitor_SMD:C_0603_1608Metric | 1 | C19702 | False | 0,0048
D1 | GREEN | ~ | LED_SMD:LED_0805_2012Metric | 1 | C2297 | False | 0,0095
D2 | RED | ~ | LED_SMD:LED_0603_1608Metric | 1 | C2286 | False | 0,0053
J1 | Au+ | ~ | 4022S:Au_Electrode | 1
J3 | Ti+ | ~ | Connector_PinHeader_2.54mm:PinHeader_1x01_P2.54mm_Vertical | 1
J4 | Au- | ~ | 4022S:Au_Electrode | 1
J6 | Ti-1 | ~ | Connector_PinHeader_2.54mm:PinHeader_1x01_P2.54mm_Vertical | 1
J7 | Ti-2 | ~ | Connector_PinHeader_2.54mm:PinHeader_1x01_P2.54mm_Vertical | 1
J8 | Debug | ~ | Connector_PinSocket_2.54mm:PinSocket_1x04_P2.54mm_Vertical | 1
J9 | RS485 | ~ | Connector_PinSocket_2.54mm:PinSocket_1x04_P2.54mm_Vertical | 1
J11 | Ti-2 | ~ | Connector_PinHeader_2.54mm:PinHeader_1x01_P2.54mm_Vertical | 1
Q1 | S8050_SMD |  | Package_TO_SOT_SMD:SOT-23-3 | 1 | C2146 | False | 0,0131
Q2 | PMOS | http://www.aosmd.com/pdfs/datasheet/AO3401A.pdf | Package_TO_SOT_SMD:SOT-23 | 1 | C15127 | False | 0,0387
Q3 | PMOS | http://www.aosmd.com/pdfs/datasheet/AO3401A.pdf | Package_TO_SOT_SMD:SOT-23 | 1 | C15127 | False | 0,0387
R1 | 10k | ~ | Resistor_SMD:R_0603_1608Metric | 1 | C25804 | False | 0,0008
R2 | 4.7k | ~ | Resistor_SMD:R_0603_1608Metric | 1 | C23162 | False | 0,0010
R3 | 4.7k | ~ | Resistor_SMD:R_0603_1608Metric | 1 | C23162 | False | 0,0010
R4 | 20 | ~ | Resistor_SMD:R_0603_1608Metric | 1 | C22950 | False | 0,0009
R5 | 20 | ~ | Resistor_SMD:R_0603_1608Metric | 1 | C22950 | False | 0,0009
R6 | 20 | ~ | Resistor_SMD:R_0603_1608Metric | 1 | C22950 | False | 0,0009
R7 | 20 | ~ | Resistor_SMD:R_0603_1608Metric | 1 | C22950 | False | 0,0009
R8 | 10k | ~ | Resistor_SMD:R_0603_1608Metric | 1 | C25804 | False | 0,0008
R9 | 300 | ~ | Resistor_SMD:R_0603_1608Metric | 1 | C23025 | False | 0,0010
R10 | 3k | ~ | Resistor_SMD:R_0603_1608Metric | 1 | C4211 | False | 0,0009
R11 | 30k | ~ | Resistor_SMD:R_0603_1608Metric | 1 | C22984 | False | 0,0009
R12 | 300 | ~ | Resistor_SMD:R_0603_1608Metric | 1 | C23025 | False | 0,0010
R13 | 3k | ~ | Resistor_SMD:R_0603_1608Metric | 1 | C4211 | False | 0,0009
R14 | 30k | ~ | Resistor_SMD:R_0603_1608Metric | 1 | C22984 | False | 0,0009
R15 | 120 | ~ | Resistor_SMD:R_0603_1608Metric | 1 | C22787 | False | 0,0010
R16 | 300 | ~ | Resistor_SMD:R_0603_1608Metric | 1 | C23025 | False | 0,0010
R17 | 3k | ~ | Resistor_SMD:R_0603_1608Metric | 1 | C4211 | False | 0,0009
R18 | 30k | ~ | Resistor_SMD:R_0603_1608Metric | 1 | C22984 | False | 0,0009
R19 | 1k | ~ | Resistor_SMD:R_1206_3216Metric | 1 | C4410 | False | 0,0027
R20 | 10k | ~ | Resistor_SMD:R_1206_3216Metric | 1 | C17902 | False | 0,0028
R21 | 1k | ~ | Resistor_SMD:R_0603_1608Metric | 1 | C21190 | False | 0,0009
R22 | 1k | ~ | Resistor_SMD:R_0603_1608Metric | 1 | C21190 | False | 0,0009
TP5 | SCL | ~ | TestPoint:TestPoint_THTPad_2.0x2.0mm_Drill1.0mm | 1
TP6 | SDA | ~ | TestPoint:TestPoint_THTPad_2.0x2.0mm_Drill1.0mm | 1
TP7 | RS485_UART | ~ | TestPoint:TestPoint_THTPad_2.0x2.0mm_Drill1.0mm | 1
TP8 | RS485_DE | ~ | TestPoint:TestPoint_THTPad_2.0x2.0mm_Drill1.0mm | 1
TP9 | 3V3 | ~ | TestPoint:TestPoint_THTPad_2.0x2.0mm_Drill1.0mm | 1
TP10 | UBDAC | ~ | TestPoint:TestPoint_THTPad_2.0x2.0mm_Drill1.0mm | 1
TP11 | DAC | ~ | TestPoint:TestPoint_THTPad_2.0x2.0mm_Drill1.0mm | 1
TP12 | AMP | ~ | TestPoint:TestPoint_THTPad_2.0x2.0mm_Drill1.0mm | 1
TP13 | SIG | ~ | TestPoint:TestPoint_THTPad_2.0x2.0mm_Drill1.0mm | 1
TP14 | CALIB | ~ | TestPoint:TestPoint_THTPad_2.0x2.0mm_Drill1.0mm | 1
TP15 | GND | ~ | TestPoint:TestPoint_THTPad_2.0x2.0mm_Drill1.0mm | 1
U1 | DAC53401 |  | Package_SON:WSON-8-1EP_2x2mm_P0.5mm_EP0.9x1.6mm | 1 | C2861165 | True | 0,6660
U2 | STM32F401RCTx | https://www.st.com/resource/en/datasheet/stm32f401rc.pdf | Package_QFP:LQFP-64_10x10mm_P0.5mm | 1 | C1339473 | True | 2,1735
U3 | 4xSwitch |  | Package_SO:TSSOP-14_4.4x5mm_P0.65mm | 1 | C128399 | True | 1,4775
U4 | SP3485EN | http://www.icbase.com/pdf/SPX/SPX00480106.pdf | Package_SO:SOIC-8_3.9x4.9mm_P1.27mm | 1 | C8963 | False | 0,3076
U5 | OP07C | https://www.analog.com/media/en/technical-documentation/data-sheets/OP07.pdf | Package_SO:SOIC-8_3.9x4.9mm_P1.27mm | 1 | C7433 | False | 0,1247
U6 | 4xSwitch |  | Package_SO:TSSOP-14_4.4x5mm_P0.65mm | 1 | C128399 | True | 1,4775
U7 | TempSensor |  | Package_CSP:WLCSP-8_1.551x2.284mm_P0.5mm | 1 | C2758003 | True | 0,5325
U8 | 4xSwitch |  | Package_SO:TSSOP-14_4.4x5mm_P0.65mm | 1 | C128399 | True | 1,4775
U9 | DepthSensor |  | 4022S:WF183DE | 1 | C20415992 | True | 0,6315
U10 | OP07C | https://www.analog.com/media/en/technical-documentation/data-sheets/OP07.pdf | Package_SO:SOIC-8_3.9x4.9mm_P1.27mm | 1 | C7433 | False | 0,1247
U11 | 4xSwitch |  | Package_SO:TSSOP-14_4.4x5mm_P0.65mm | 1 | C128399 | True | 1,4775

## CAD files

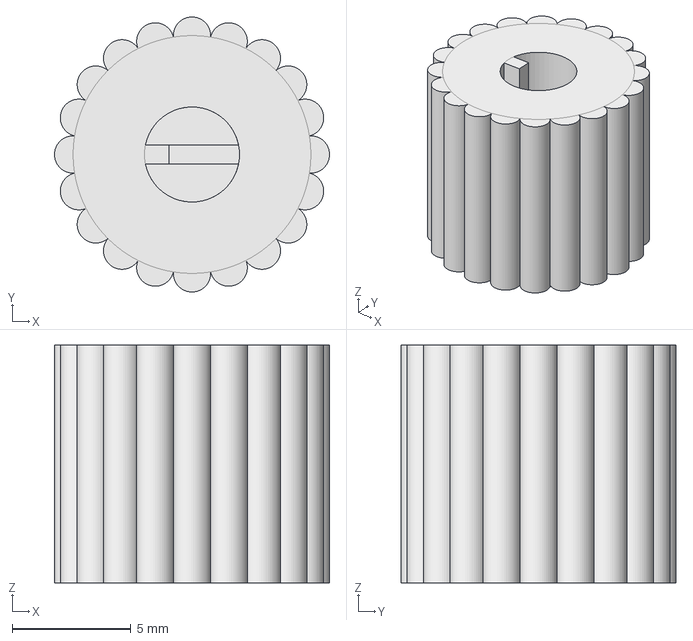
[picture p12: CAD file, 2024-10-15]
CAD/switch_cap.FCStd
11.6 x 11.6 x 10.0 mm

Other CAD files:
CAD/switch_cap.stl

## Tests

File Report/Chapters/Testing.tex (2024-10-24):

% ----------------------------------------------------
% Methodology
% ----------------------------------------------------

\chapter{Salinometer Evaluation and Testing}\label{ch:testing}

\section{Overview}

Several tests were conducted to evaluate the salinometer.
The tests experimentally verified the accuracy of the individual components, evaluated the salinometer's interaction with saltwater samples and determined its ability and accuracy in measuring salinity.
The tests were conducted in two phases because some required access to the board's circuitry and test points, while others required the probe to be exposed to salt water, which could only happen after the probe was cast in epoxy.
The first phase involved evaluating the \gls{dac}, \gls{adc}, calibration resistor and resistance measuring accuracy which is covered in \refsec{sec:dac-voltage-range-and-accuracy} to \refsec{sec:resistance-measuring-accuracy}.

After the first testing phase, the probe was cast into epoxy resin as described in \refsec{sec:probe-epoxy-casting}, which allowed the second phase to commence.
First, the pressure sensor was tested, and it was confirmed to be working as expected, returned accurate temperature and pressure readings.
The second phase involved establishing a voltage-resistance relationship for the salt water, a voltage-to-conductivity relationship for both electrodes and finally, the salinometer's ability to measure salinity, which is covered in \refsec{sec:voltage-sweep-repeatability} to \refsec{sec:ac-voltage-measurements}.
No corrosion nor electrolysis was noticed during these tests, proving that the choice of materials and the bidirectional measurements were effective at preventing these issues.
A summary of these tests is shown in \reftbl{tab:testing-summary}, and each test is discussed in further detail in its relevant section.

%chktex-file 44
\begin{longtblr}[
    caption = {A summary of the evaluation and testing of the salinometer.},
    label = {tab:testing-summary}
    ]{
    hlines,
    vlines,
    colspec = {Q[c,m]X[c,m]Q[c,m,2.5cm]Q[c,m,1.75cm]Q[c,m,2.5cm]}
    }
    \textbf{Sec.} & \textbf{Test Description} & \textbf{Result Metric} & \textbf{Ideal Result} & \textbf{Measured Results} \\
    \ref{sec:dac-voltage-range-and-accuracy} & The minimum and maximum voltage output of the \gls{dac} between $0V$ and $V_{DD} = 3,3V$ & Range & $0-3,3V$ & $0-2,59V$ \\
    \ref{sec:dac-voltage-range-and-accuracy} & The gain and offset of the output voltage of the \gls{dac} relative to the instructed voltage & {Gain \\ Offset} & {$1,0$ \\ $0,0V$} & {$0,9837$ \\ $0,0070V$} \\
    \ref{sec:adc-accuracy} & The gain and offset of the voltage measured by the \gls{adc} relative to the voltage measured by the multimeter & {Gain \\ Offset} & {$1,0$ \\ $0,0V$} & {$0,9877$ \\ $0,0082V$} \\
    \ref{sec:calibration-resistance} & The resistance of the calibration resistor & Resistance & $5\Omega$ & $5,00\Omega$ \\
    \ref{sec:resistance-measuring-accuracy} & The gain and offset of the resistance measured by the salinometer relative to the resistance measured by the multimeter & {Gain \\ Offset} & {$1$ \\ $0\Omega$} & {$1,0000$ \\ $0,0000\Omega$} \\
    {\ref{sec:voltage-sweep-repeatability}, \\ \ref{sec:voltage-conductivity-mapping}} & The repeatability of voltage sweep measurements, the difference between measurements of different samples, and the accuracy of the calculated salinity & {Repeatability \\ Differentiability \\ Accuracy} & {Identical \\ Clear \\ Accurate} & {Within $10\%$ \\ Clear \\ Inaccurate} \\
    \ref{sec:individual-voltage-measurements} & The repeatability of individual voltage measurements, the difference between measurements of different samples, and the accuracy of the calculated salinity & {Repeatability \\ Differentiability \\ Accuracy} & {Identical \\ Clear \\ Accurate} & {Within $10\%$ \\ Clear \\ Within 4 \gls{psu}} \\
    \ref{sec:ac-voltage-measurements} & The repeatability of \gls{ac} voltage measurements, the difference between measurements of different samples, and the accuracy of the calculated salinity & {Repeatability \\ Differentiability \\ Accuracy} & {Identical \\ Clear \\ Accurate} & {Untested \\ Unclear \\ -} \\
\end{longtblr}

\section{Testing Apparatus}

Voltage and resistance measurements were taken on the probe using a bench multimeter.
The most accurate multimeter available was a \textit{Keysight Technologies} U3401A, shown in \reffig{fig:bench-multimeter}, which had voltage accuracy of $0,02\%$ and resistance accuracy of $0,1\%$.
In order to test the probe \gls{pcb}, voltage probes were connected to the test points, shown in \reffig{fig:probe-experiments}, or they were connected directly to the components.

\begin{figure}[ht]
    \begin{minipage}{0.5\textwidth}
        \centering
        
        \caption{The salinometer probe with multimeter cables attached to a test point and ground.}
        \label{fig:probe-experiments} %chktex 24
    \end{minipage}
    \begin{minipage}{0.5\textwidth}
        \centering
        
        \caption{The bench multimeter used for the tests displaying a voltage reading.}
        \label{fig:bench-multimeter} %chktex 24
    \end{minipage}
\end{figure}

\section{DAC Voltage Range and Accuracy}\label{sec:dac-voltage-range-and-accuracy}

The transistor buffer configuration explained in \refsec{sec:dac-voltage-range-and-accuracy} has one disadvantage: the output voltage of the system is limited by the transistor's $V_{BE}$ where the highest possible voltage output is $V_{DD} - V_{BE}$.
According to the transistor's \href{https://www.lcsc.com/datasheet/lcsc_datasheet_2310131500_Jiangsu-Changjing-Electronics-Technology-Co---Ltd--S8050-J3Y-RANGE-200-350_C2146.pdf}{data sheet}, the buffered output should be limited to $3,3V - 0,6V = 2,7V$ when conducting $0A$ and $3,3V - 0,75V = 2,55V$ when conducting the circuit's maximum current of $33mA$.
In order to assess the range and accuracy of the \gls{dac}, it was instructed to output voltages from $0V$ to $V_{DD} = 3,3V$ in intervals of 64-bit. 
The output voltage was measured at the base and emitter of the transistor, with no load and a maximum load of $100\Omega$.
The results were graphed and shown in~\reffig{fig:dac-voltage-range-no-load} and~\reffig{fig:dac-voltage-range-loaded}.

\begin{figure}[ht]
    \centering
    \begin{minipage}{.5\textwidth}
        \centering
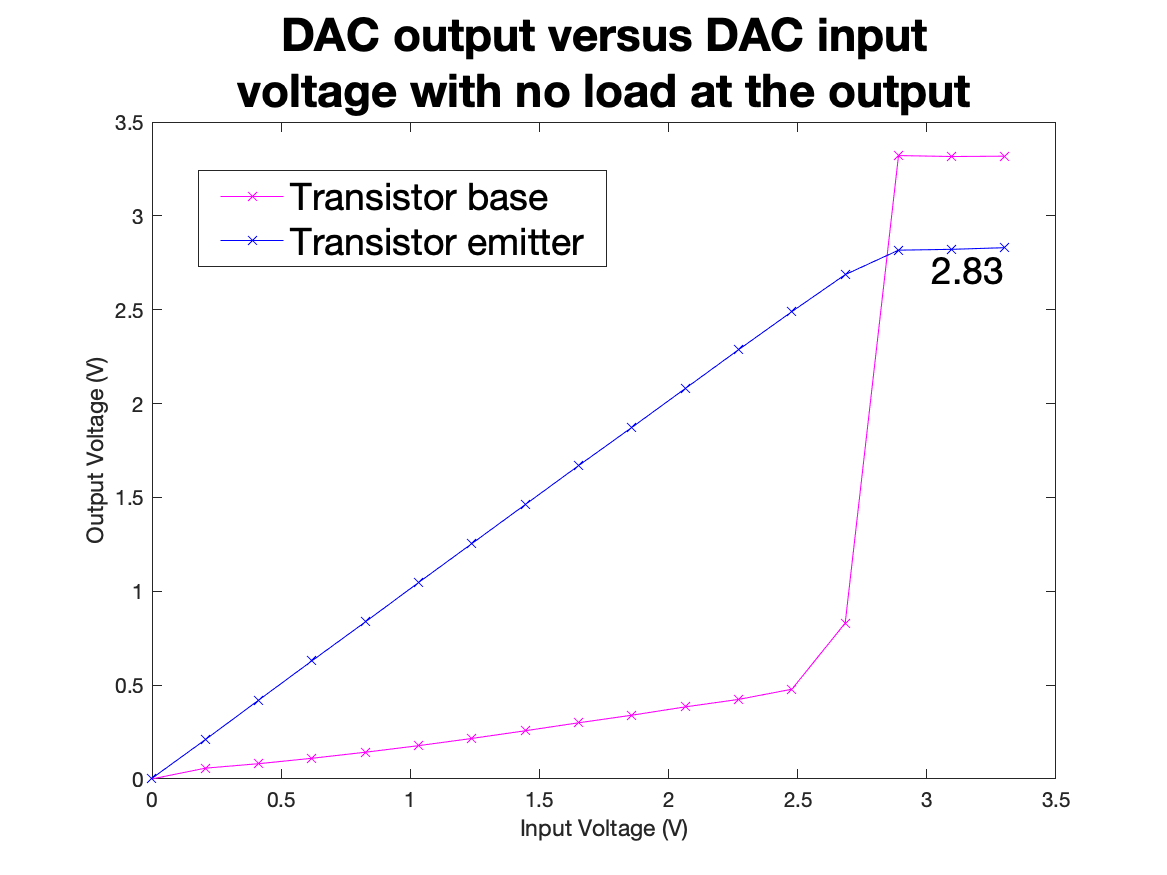
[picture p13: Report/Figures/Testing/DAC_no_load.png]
        
        \caption{The input voltage versus the output voltage of the \gls{dac} with no load.}
        \label{fig:dac-voltage-range-no-load} %chktex 24
    \end{minipage}%
    \begin{minipage}{.5\textwidth}
        \centering
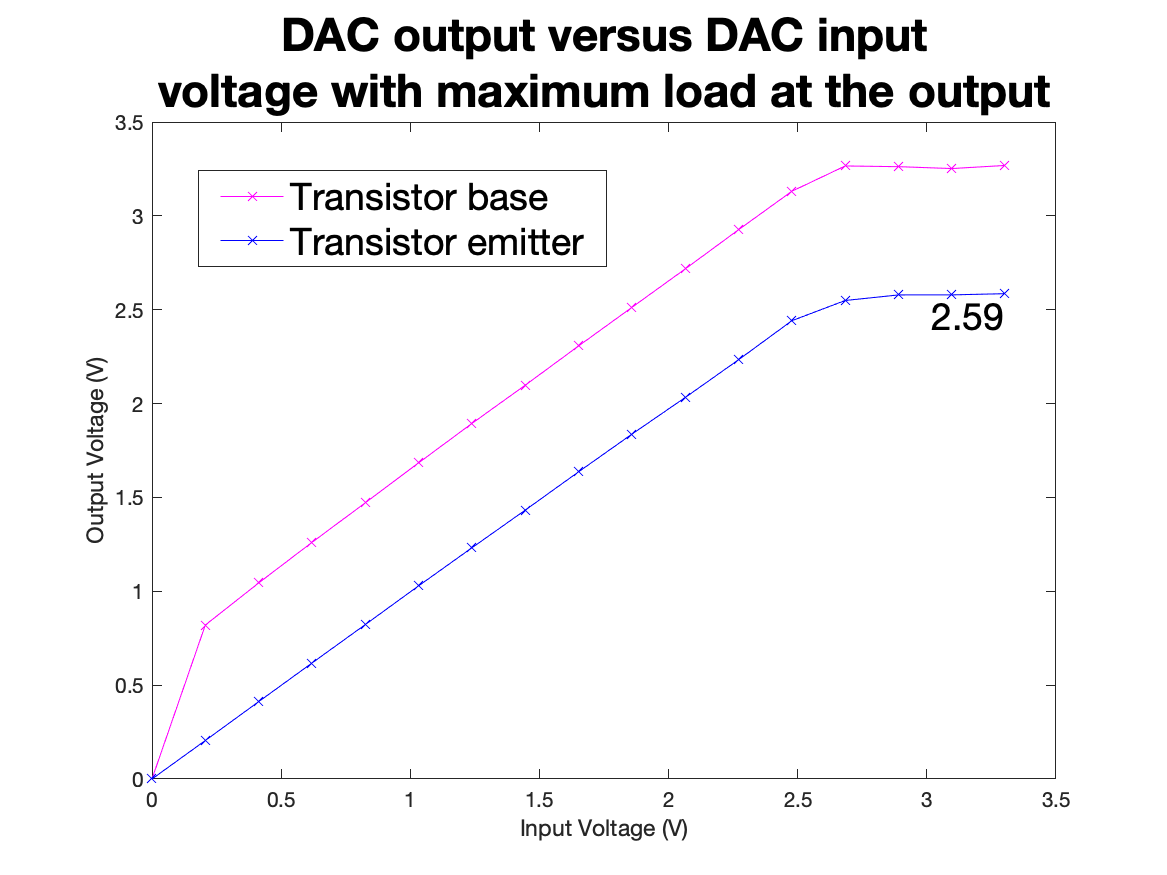
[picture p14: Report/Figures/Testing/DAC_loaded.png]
        
        \caption{The input voltage versus the output voltage of the \gls{dac} with the maximum load of $100\Omega$.}
        \label{fig:dac-voltage-range-loaded} %chktex 24
    \end{minipage}
\end{figure}

The voltage drop due to $V_{BE}$ can clearly be seen on~\reffig{fig:dac-voltage-range-loaded}.
The unloaded output voltage reached $2,83V$, and the loaded output voltage reached $2,59V$, which were slightly higher than the predicted limits.

An alternative attempt was made to achieve a higher voltage output using the \gls{dac}'s internal voltage reference of $1,21V$ multiplied by a gain of $4$, resulting in a reference of $4,84V$.
As expected, this did not increase the output voltage; the base of the transistor continued to measure $3,3V$ and the emitter $2,83V$ while unloaded.

Due to the voltage limitations, the \gls{dac} was limited to $2,6V$ for future testing and implementation.
When excluding the voltage readings above $2,6V$, the \gls{dac} achieved a gain of $0,9837V/V$ and an offset $+0,0070V$ between the input voltage and measured voltage under maximum load. 
\section{ADC Accuracy}\label{sec:adc-accuracy}

The \gls{adc} was tested by measuring a range of voltages produced by the \gls{dac} and comparing them to the multimeter's measurement.
The \gls{adc} was configured in 12-bit mode, with each measurement taking 15 \gls{adc} clock cycles, equivalent to $250ns$ with the $16MHz$ system clock.
$5$ measurements were taken and averaged for each voltage outputted by the \gls{dac} to increase the accuracy of each measurement.
The results were graphed and shown in~\reffig{fig:adc-accuracy}. 

\begin{figure}[ht]
    \centering
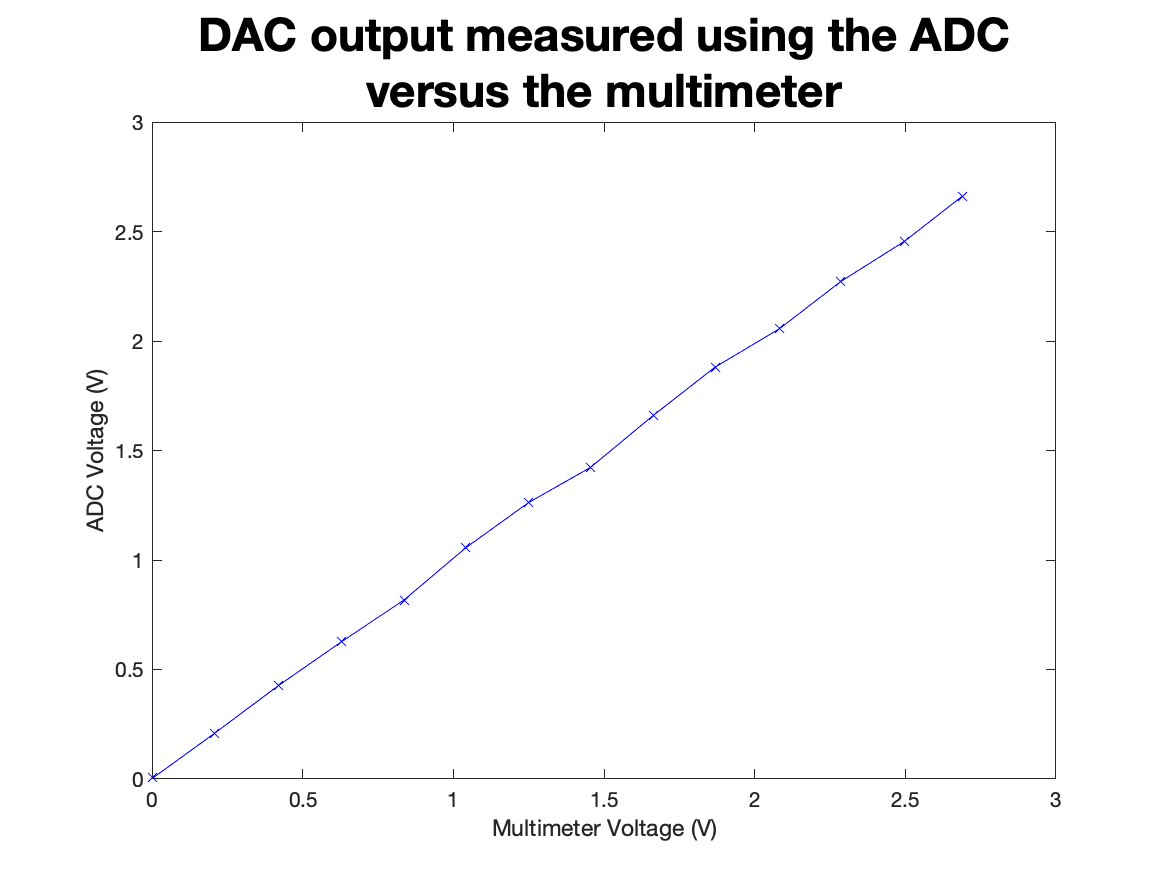
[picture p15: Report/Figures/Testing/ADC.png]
    
    \caption{The voltage output by the \gls{dac} measured by a multimeter versus by the \gls{adc}.}
    \label{fig:adc-accuracy} %chktex 24
\end{figure}

The \gls{adc} achieved a gain of $0,9877V/V$ and an offset of $0,0082V$ compared to the multimeter.

\section{Calibration Resistance}\label{sec:calibration-resistance}

The multimeter measured the calibration resistor by directly connecting its probes to the four parallel resistors.
The calibration resistor was electrically disconnected from the rest of the circuit during the measurement.
The calibration resistance was specified to be $5\Omega \pm 0,25\%$; thus, its actual value could range between $4,9875$ and $5,0125\Omega$.

The multimeter measured the calibration resistor to be $5,25\Omega$.
However, the multimeter probes measured $0,25\Omega$ when short-circuited.
Thus, the actual resistance was calculated as $5,00\Omega$.
It should be noted that the multimeter can only display to the nearest $0,01\Omega$.
Thus, the actual resistance could range from $4,995\Omega$ to $5,005\Omega$, and more precise equipment would be required to obtain a more accurate measurement.

\section{Resistance Measuring Accuracy}\label{sec:resistance-measuring-accuracy}

The probe's accuracy in measuring resistance was determined by comparing its calculated resistance to the multimeter's measurement of a given resistor.
The probe calculated resistance by measuring the voltage drop across the resistor attached between the titanium electrode ports and the calibration resistor. 
Then, it calculated its resistance per \refeqn{eqn:parallel-resistor-total} to \refeqn{eqn:parallel-resistor-uncertainty}.

For this test, the probe measured resistance using two methods: one with a single voltage provided by the \gls{dac} of $V_{DD}/2 = 1,65V$ and one with voltage sweep from the \gls{dac} with $50$ samples.
In the latter case, the resistances were calculated for each sample and averaged.
At low voltages, single-bit errors caused significant changes in the calculated resistance, which were avoided by limiting the voltage sweep to between $0,3V$ and $2,6V$.
The resistors used had a range of $0\Omega$, or a short-circuit, to $10\Omega$ as this is the expected range for the gold electrodes.
The results of the voltage sweep versus the multimeter test are shown in~\reffig{fig:resistance-measuring-accuracy-uncorrected}. 

\begin{figure}[!ht]
    \centering
    \begin{minipage}{.5\textwidth}
        \centering
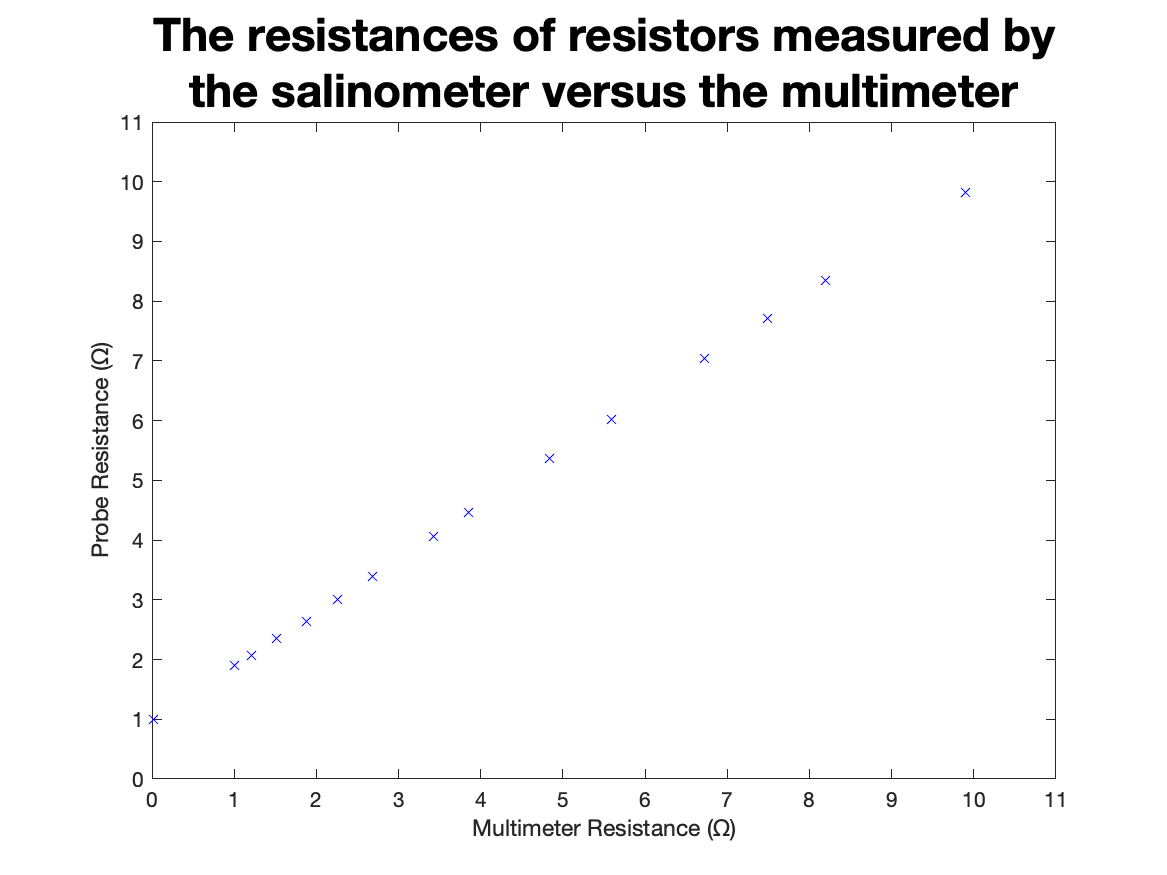
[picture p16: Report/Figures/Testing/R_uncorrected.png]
        
        \caption{The resistance measuring test.}
        \label{fig:resistance-measuring-accuracy-uncorrected} %chktex 24
    \end{minipage}%
    \begin{minipage}{.5\textwidth}
        \centering
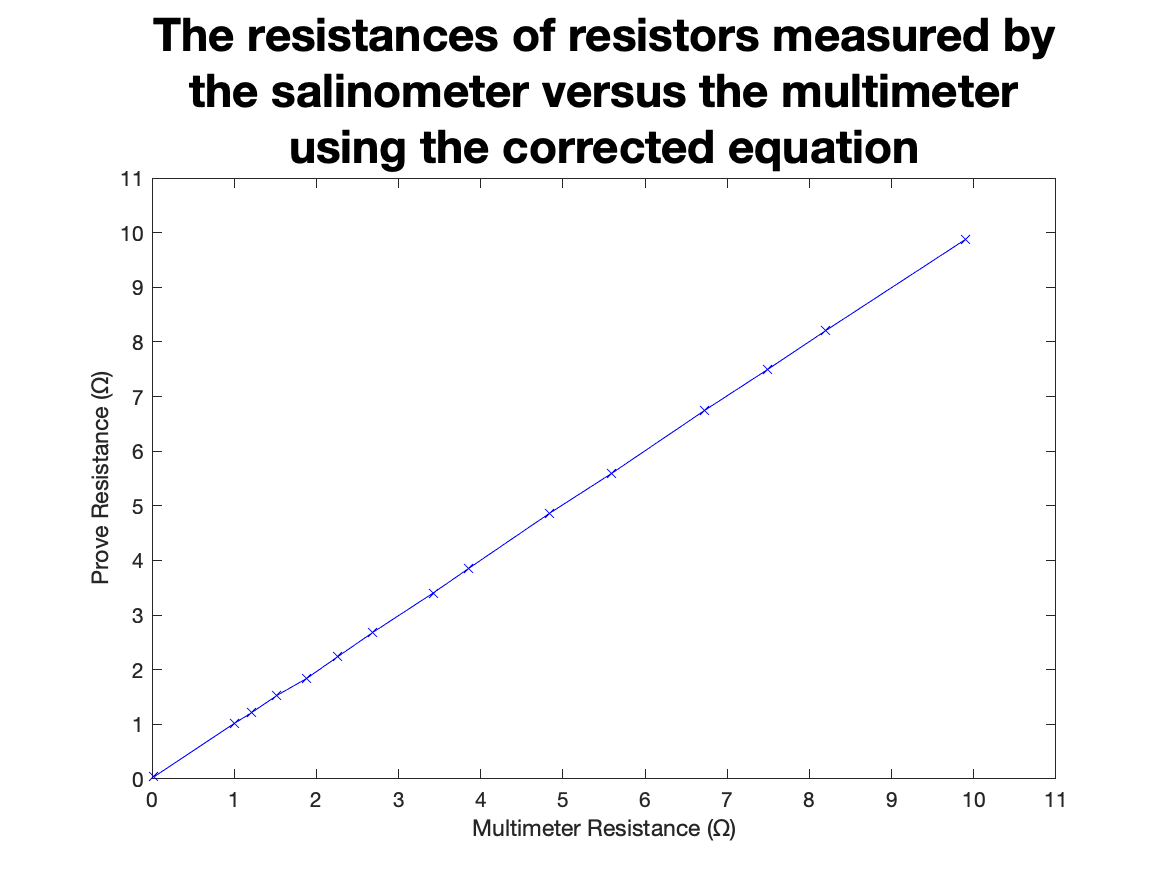
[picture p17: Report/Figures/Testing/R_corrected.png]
        
        \caption{The resistance measuring test using the corrected equation.}
        \label{fig:resistance-measuring-accuracy-corrected} %chktex 24
    \end{minipage}
\end{figure}

The single voltage and voltage sweep methods were perfectly correlated with an $r^2$ value of $1,0000$.
However, there was a clear error between the probe's and the multimeter's measurements.
This error was assumed to be due to the unaccounted resistance of the switches and the traces.
While these values could be measured and included in the equation, a more efficient and arguably more accurate method would be to generate an equation of best fit and use it to calculate the correct resistance.

To determine the general formula of the equation of best fit, \refeqn{eqn:electrode-calib-resistance} with the electrode resistance $R_E$ and the calibration resistance $R_C$, was adjusted to include $r_e$, which represents the unknown resistance of the switches and traces as shown in \refeqn{eqn:resistance-measuring}.
$R_C$, $R_1$ and $r_e$ were condensed into the standard rational function coefficients $p$ and $q$ as shown in \refeqn{eqn:resistance-measuring-rational}.
Finally, the equation was rearranged to give the electrode's resistance in terms of the measured voltage ratio as shown in \refeqn{eqn:resistance-measuring-rational}.

\begin{align}
 V_{ratio} &= \lfrac{\lfrac{R_E + r_{e1}}{R_E + R_1 + r_{e2}}}{\lfrac{R_C + r_{e3}}{R_C + R_1 + r_{e4}}} \nonumber \\
    &= \lfrac{R_E + r_{e1}}{R_E + R_1 + r_{e2}} \times \lfrac{R_C + R_1 + r_{e4}}{R_C + r_{e3}} \label{eqn:resistance-measuring} \\
 V_{ratio} &= \lfrac{p_1 R_E + p_2}{R_E + q_1} \label{eqn:resistance-measuring-rational} \\
 R_E &= \lfrac{p_2 - q_1 V_{ratio}}{V_{ratio} - p_1} \label{eqn:resistance-measuring-rearranged}
\end{align}

The \refeqn{eqn:resistance-measuring-rational} of best fit was confirmed using MATLAB, which gave the values $p_1 = 17,4687$, $p_2 = 18,4643$ and $q_1 = 91,8315$ with an $r^2$ value of $1,0000$. 
The corrected resistance values were obtained from the previous data set by reversing the previous formula and applying \refeqn{eqn:resistance-measuring-rearranged} to the voltage ratios.
These results were graphed and are shown in \reffig{fig:resistance-measuring-accuracy-corrected} and have a gain of $1,0000$ and an offset of $0,0000$.
Note that this correction equation is only valid when $R_1$ is $100\Omega$ and separate equations will need to be generated should different values of $R_1$ be needed.

\section{Voltage Sweep Repeatability}\label{sec:voltage-sweep-repeatability}

The following tests investigate a method for producing repeatable voltage measurements of a saltwater sample.
In order to conduct these tests, the probe was cast into epoxy as described in \refsec{sec:probe-epoxy-casting}.

The tests were configured with parameters such as which electrodes to use, the voltage sample count, the \gls{adc} sample count and the \gls{dac} range.
Due to a circuit error discovered after the epoxy casting, the gold electrodes could only be used with the fringe guard.
Thus, the effectiveness of the fringe guard was unable to be tested.
Each voltage sweep results were transmitted over \gls{uart} to a computer, where they were processed using Microsoft Excel and MATLAB to generate graphs and metrics.

The first test was a voltage sweep performed both forwards and in reverse with increasing and decreasing \gls{dac} voltages respectively.
The test was configured with the gold electrodes and the fringe guard, 50 voltage samples, 2 \gls{adc} samples and a voltage range of $0-2,6V$.
It was performed on a salt water sample of unknown salinity around 30 \gls{psu}.
Ideally, the two sweeps should have been identical.
However, they were not, as shown in \reffig{fig:test1}.

\begin{figure}[ht]
    \begin{minipage}{0.5\textwidth}
        \centering
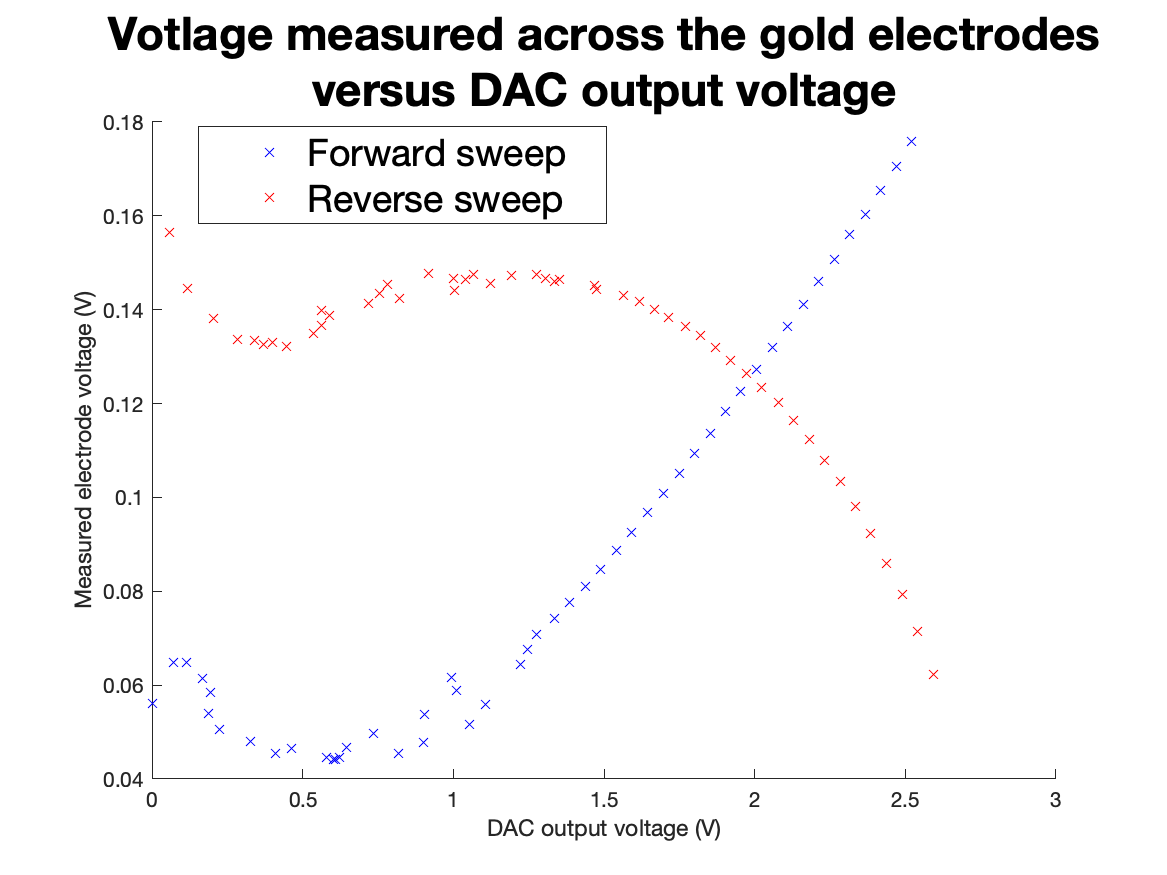
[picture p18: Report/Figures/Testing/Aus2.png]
        
        \caption{Voltage sweep repeatability test 1 with gold electrodes and the fringe shield, a voltage range of $0-2,6V$, and 50 samples taken of salt water sample of unknown salinity.}
        \label{fig:test1} %chktex 24
    \end{minipage}
    \begin{minipage}{0.5\textwidth}
        \centering
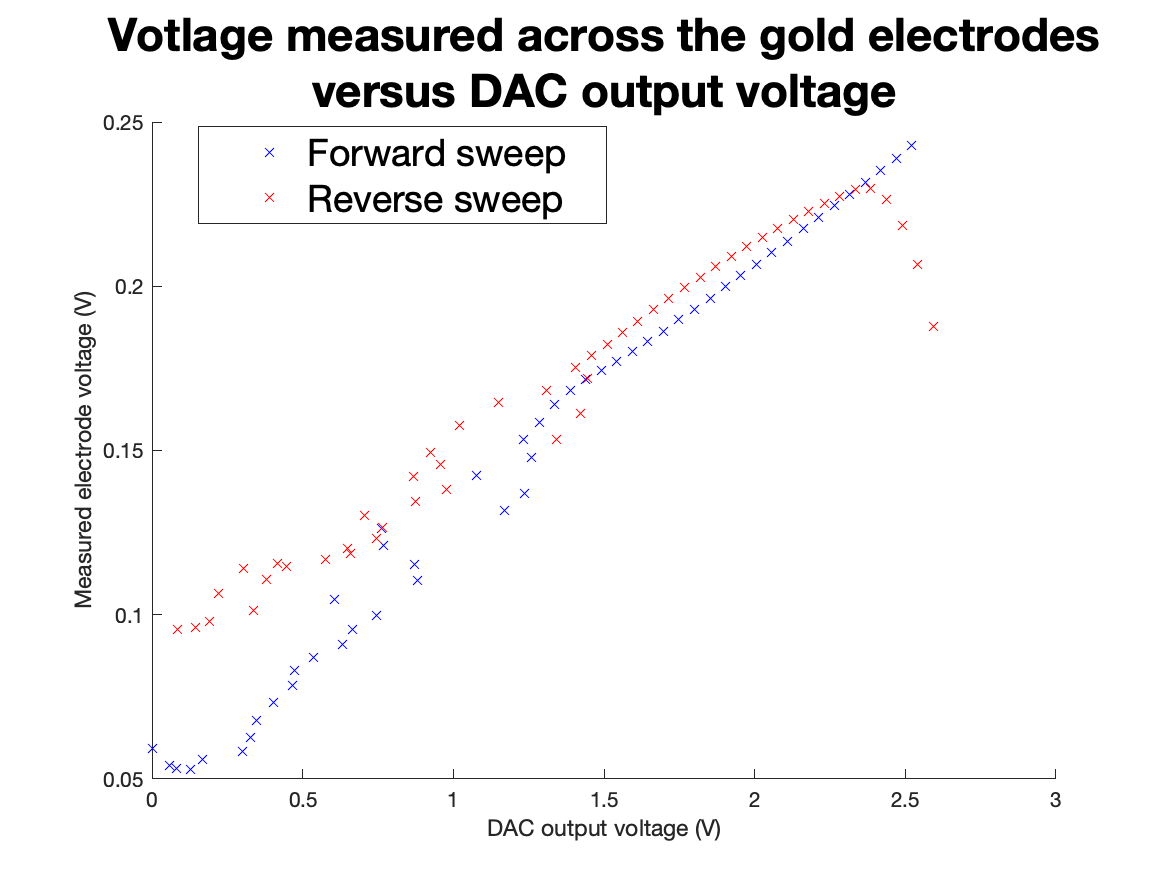
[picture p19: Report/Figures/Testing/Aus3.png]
        
        \caption{Voltage sweep repeatability test 2 with draining and resetting the \gls{dac} between each voltage sample.}
        \label{fig:test2} %chktex 24
    \end{minipage}
\end{figure}

To further investigate the inconsistency, the \gls{dac} was reset to $0V$ before it was set to the desired voltage for each sample.
It should be noted that the \gls{dac} reset added a slight delay between each voltage sample of around $10ms$. 
While this did make the forward and reverse sweeps more similar, as shown in \reffig{fig:test2}, the initial voltage lag of the reverse sweep on the right hand-side of the graph was still present.

It was theorised that the measurements of the water briefly altered its properties, which in turn altered the proceeding measurements.
This alteration was unlikely to be a capacitive effect, as the measurements were taken bidirectionally, which would have dissipated any built-up charge.
It was possible that the voltage was dissociating the dissolved material into ions, allowing the charges in the salt water sample to move more freely and alter the measurement~\cite{ostdiek_inquiry_into_physics_2020}.
However, determining exactly what caused the alteration was beyond the scope of this project.

Instead, to further investigate this, a test was conducted taking priming measurements at the maximum voltage of $2,6V$ before capturing the actual measurements.
The priming caused the actual measurements in both directions to start high and progressively move to their predicted paths, as shown in \reffig{fig:test3}.

\begin{figure}[ht]
    \begin{minipage}{0.5\textwidth}
        \centering
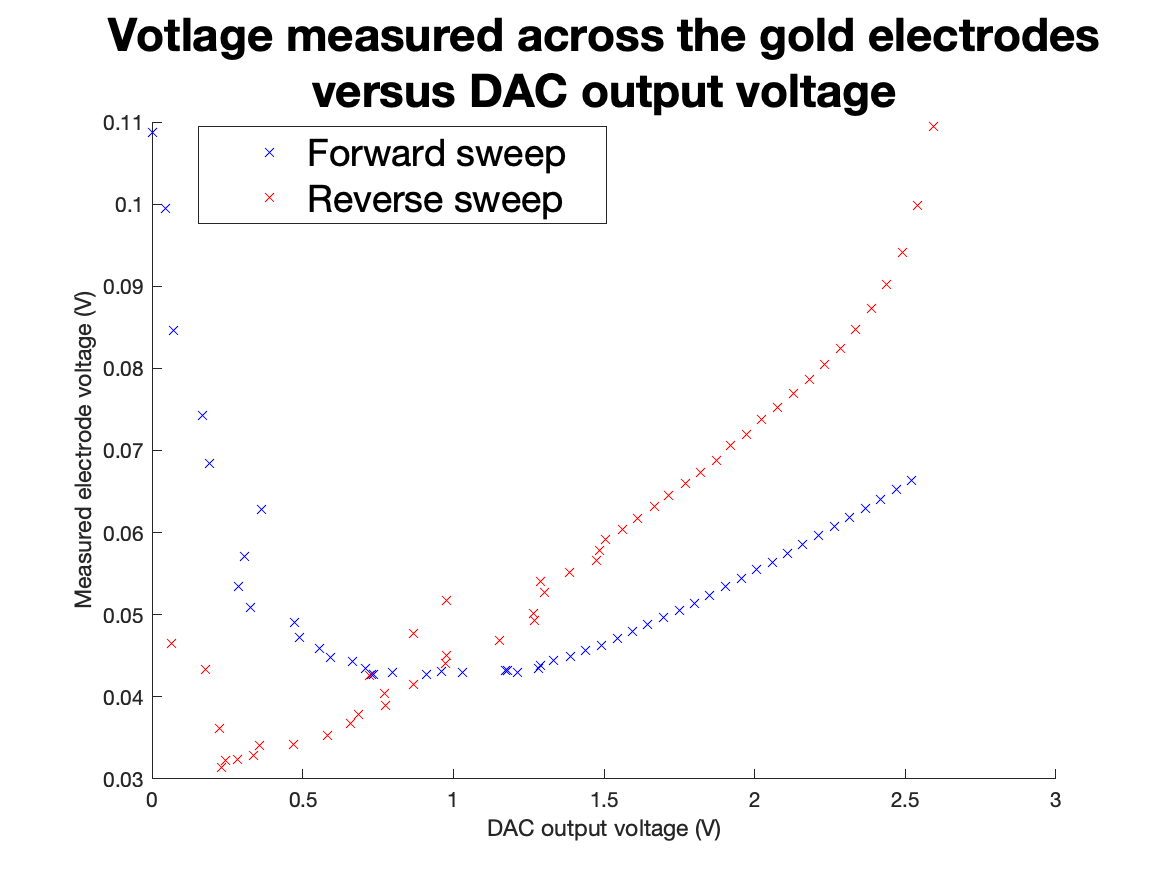
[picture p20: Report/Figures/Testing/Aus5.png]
        
        \caption{Voltage sweep repeatability test 3 with 25 priming measurements taken before the actual measurement.}
        \label{fig:test3} %chktex 24
    \end{minipage}
    \begin{minipage}{0.5\textwidth}
        \centering
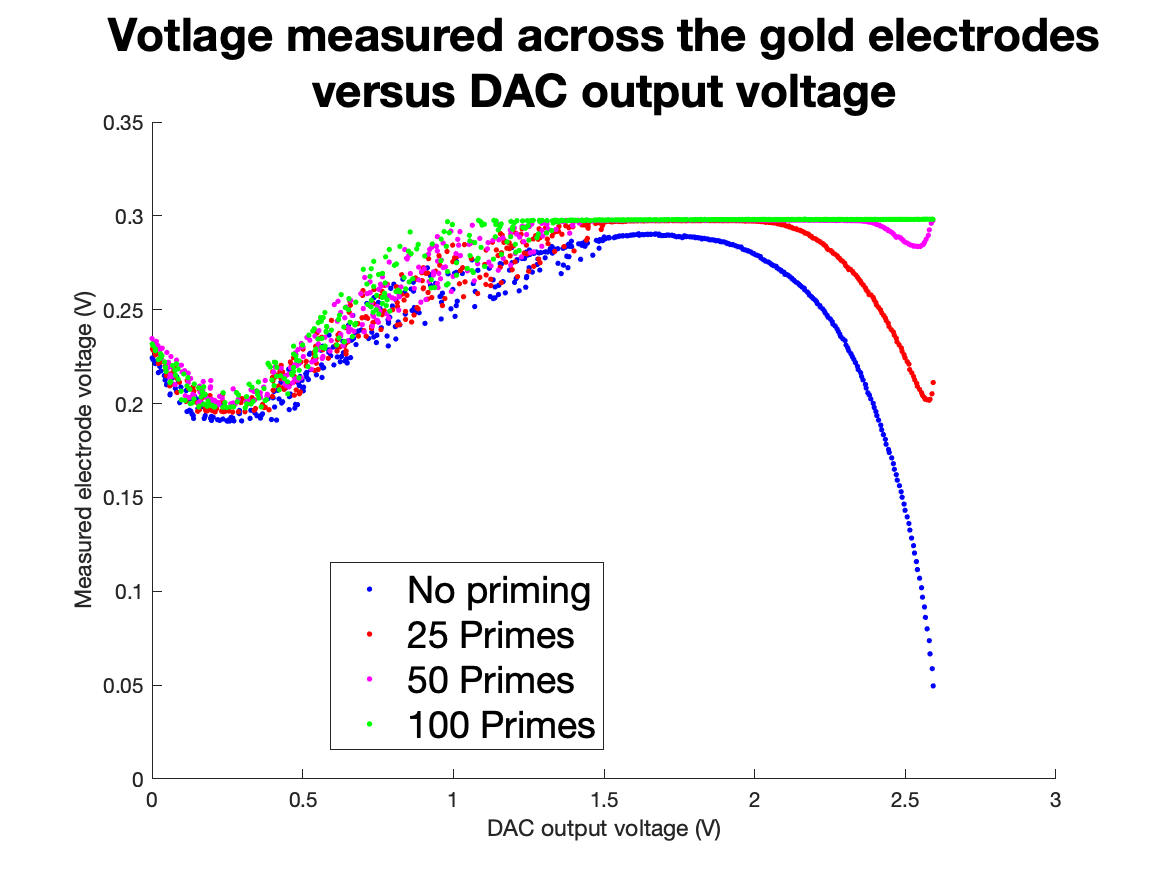
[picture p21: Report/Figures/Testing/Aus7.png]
        
        \caption{Voltage sweep repeatability test 4 with a varying number of priming measurements and the actual measurement taken as reverse voltage sweeps with 500 voltage samples.}
        \label{fig:test4} %chktex 24
    \end{minipage}
\end{figure}

This result supported the theory that the measurements were affecting the water.
The next test varied the number of priming measurements and used 500 voltage samples to increase the curve's resolution, as shown in \reffig{fig:test4}.
It should be noted that the voltage measurement effectively clipped at $0,3V$ as the output of the $11\times$ gain op-amp reached $0,3\times 11 = 3,3V$, which is the maximum voltage it can output.

While it was theoretically possible to perfectly prime a measurement, it was considered impractical, and it was also unlikely that the priming would have zero impact on the actual measurements.
Thus, voltage priming was not considered a viable solution for making repeatable measurements.
These results also indicated that a voltage measurement could be vulnerable to the priming effect from the previous measurement, which would cause undesirable effects.
Thus, an alternative method was needed to take the measurements.

It was noticed that the priming effect decreased over time, allowing the voltage sweeps in \reffig{fig:test3} to return to their expected curves.
A new theory stemmed from this that the water could relax from a primed state over time.
To test this, a delay, or relaxation time, was added between voltage samples, during which no voltage was applied to the electrodes.
The first test used relaxation times of $2s$ and $500ms$ and stirring to cycle the water between the electrodes.
With a $2s$ relaxation time, the forward and reverse voltage sweeps were near identical, as shown in \reffig{fig:test5}.
However, with a $500ms$ relaxation time, there was a clear difference and the same initial voltage lag shown in \reffig{fig:test2}.

\begin{figure}[ht]
    \begin{minipage}{0.5\textwidth}
        \centering
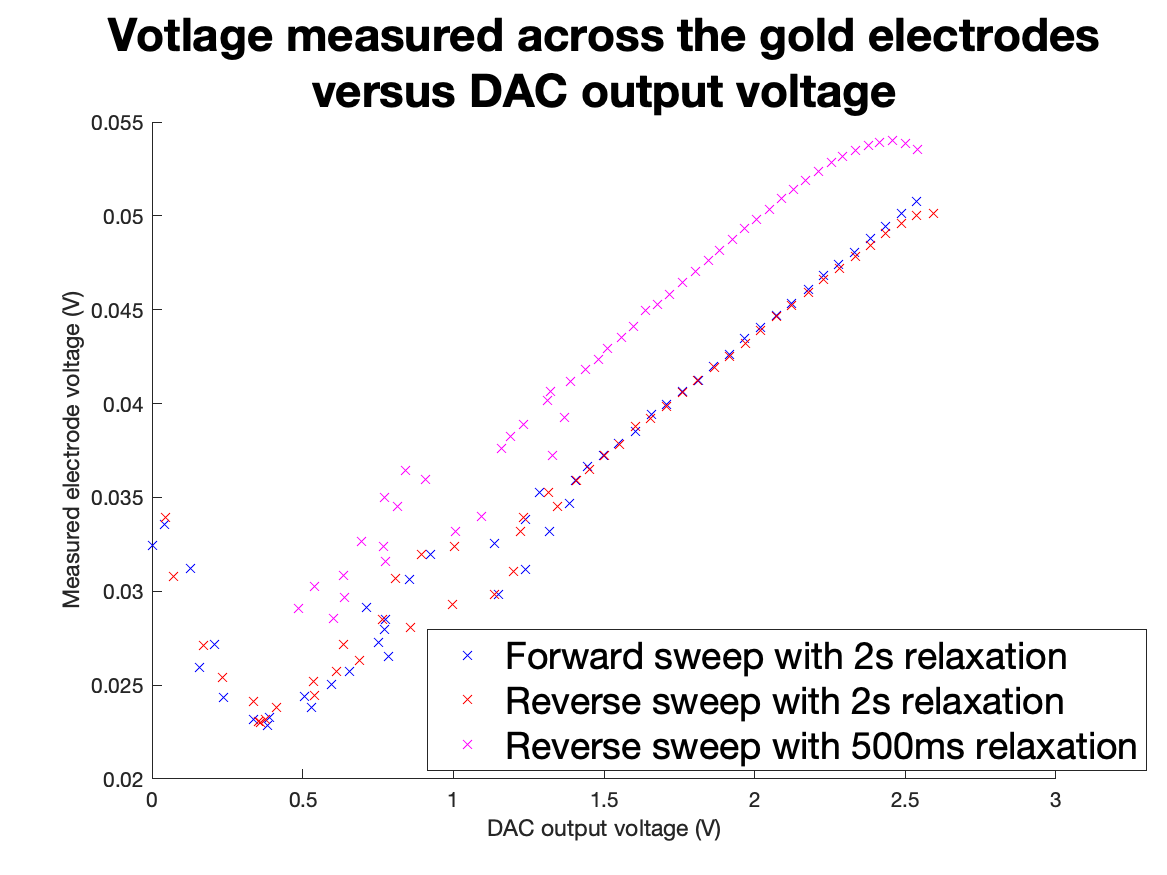
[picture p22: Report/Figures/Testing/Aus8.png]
        
        \caption{Voltage sweep repeatability test 5 with a varying amount of relaxation time before each measurement was taken and 50 samples.}
        \label{fig:test5} %chktex 24
        \end{minipage}
    \begin{minipage}{0.5\textwidth}
        \centering
        
        \caption{Voltage sweep repeatability test 6 with the difference between the titanium and gold electrodes.}
        \label{fig:test6} %chktex 24
    \end{minipage}
\end{figure}
This test concluded a valid method of measuring a voltage sweep, which used a relaxation time of $2s$ between each voltage sample.
This method allowed the titanium electrodes' length and spacing to be experimentally configured such that they could use the same $R_1$ value of $100\Omega$ as the gold electrodes.
Iterative testing revealed that a length of $30mm$ and a spacing of $6mm$ used most of the $0V$ to $0,3V$ range available to the electrodes.
A test comparing the titanium and gold electrodes was performed using a relaxation time of $2s$, shown in \reffig{fig:test6}.
The results showed that the gold electrodes followed the same curve that \refref{benjankar_ec_based_salt_measurement_2021} found, while the titanium electrodes did not.
The reason for this is unknown; it was theorised that the titanium electrodes' fringing effect and conductivity difference were the cause, but this required further investigation.

The investigation into determining a repeatable voltage sweep necessitated two more tests: the repeatability of the sweep on the same sample and the differentiation between samples.
The former involved taking two voltage sweeps of two different saltwater samples of unknown but different salinities, shown in \reffig{fig:test7}.
These results showed that the voltage sweeps were approximately grouped by salinity, allowing for a clear differentiation between the two samples despite the noise in the measurements.

\begin{figure}[ht]
    \begin{minipage}{0.5\textwidth}
        \centering
        
        \caption{Voltage sweep repeatability test 7 with 4 identical tests of 20 samples with 2s of relaxation time between measurements.}
        \label{fig:test7} %chktex 24
    \end{minipage}
    \begin{minipage}{0.5\textwidth}
        \centering
        
        \caption{Voltage sweep repeatability test 8 with 4 identical tests of 20 samples with 2s of relaxation time between measurements.}
        \label{fig:test8} %chktex 24
    \end{minipage}
\end{figure}

Next, an individual measurement's repeatability was further investigated by taking four identical voltage sweeps of the same saltwater sample.
The results, shown in \reffig{fig:test8}, found that the measurements were approximately grouped.
However, it was noticed that the voltage sweeps drifted upwards with each successive measurement.
A higher voltage sweep indicated a higher resistance, lower conductivity, and thus a lower salinity.
This was likely due to the previous sweep affecting the proceeding one, similar to the priming effect.
A test that could isolate both issues would be replacing the water between the electrodes during the voltage sweep.
This could be achieved using a pump and a large volume of water of known salinity, similar to how \href{https://oceanexplorer.noaa.gov/technology/ctd/ctd.html}{Ocean Exploration's CTD} operate. 
However, this apparatus was not available to this project.

It was noticed that there was a measurement inconsistency of the voltage samples below $1,5V$, which is visible in \reffig{fig:test5}.
However, the same inconsistency was present in the measurement and calibration reading. 
Thus, it was likely due to noise in the \gls{adc} or op-amp.
A similar inconsistency was present at the end of the voltage range, shown in \reffig{fig:test6}, likely due to the voltage lag of the reverse sweep.
To allow for a more straightforward analysis, these voltages were excluded.

\section{Voltage to Conductivity Mapping}\label{sec:voltage-conductivity-mapping}
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

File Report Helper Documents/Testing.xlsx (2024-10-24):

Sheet: DAC Range
VDD | 3.3244 | 3.2737 | 3.29905
GND | 0.0000
 |  | no load |  | loaded
DAC input | `@ 3v3 | dac | buff_dac | dac | buff_dac
0 | 0 | 0.00029 | 0.00384 | 0.00029 | 2e-05
64 | 0.2064516129 | 0.05771 | 0.20963 | 0.8202 | 0.20509
128 | 0.4129032258 | 0.08159 | 0.42009 | 1.0443 | 0.41189
192 | 0.6193548387 | 0.1104 | 0.6297 | 1.2606 | 0.6178
256 | 0.8258064516 | 0.14257 | 0.8366 | 1.4713 | 0.8227
320 | 1.032258065 | 0.17767 | 1.0469 | 1.6842 | 1.0291
384 | 1.238709677 | 0.21611 | 1.2543 | 1.8941 | 1.2318
448 | 1.44516129 | 0.25702 | 1.462 | 2.0981 | 1.4325
512 | 1.651612903 | 0.29951 | 1.6696 | 2.307 | 1.6364
576 | 1.858064516 | 0.3399 | 1.8732 | 2.5125 | 1.8371
640 | 2.064516129 | 0.38418 | 2.0801 | 2.7173 | 2.0325
704 | 2.270967742 | 0.42398 | 2.287 | 2.9261 | 2.2334
768 | 2.477419355 | 0.47831 | 2.4899 | 3.131 | 2.4415
832 | 2.683870968 | 0.8307 | 2.6869 | 3.2658 | 2.5491
896 | 2.890322581 | 3.3212 | 2.8172 | 3.262 | 2.5788
960 | 3.096774194 | 3.3161 | 2.8217 | 3.252 | 2.579
1023 | 3.3 | 3.318 | 2.8304 | 3.2683 | 2.5854
DAC max with internal 4x 1.21V |  |  |  | 3.8323
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

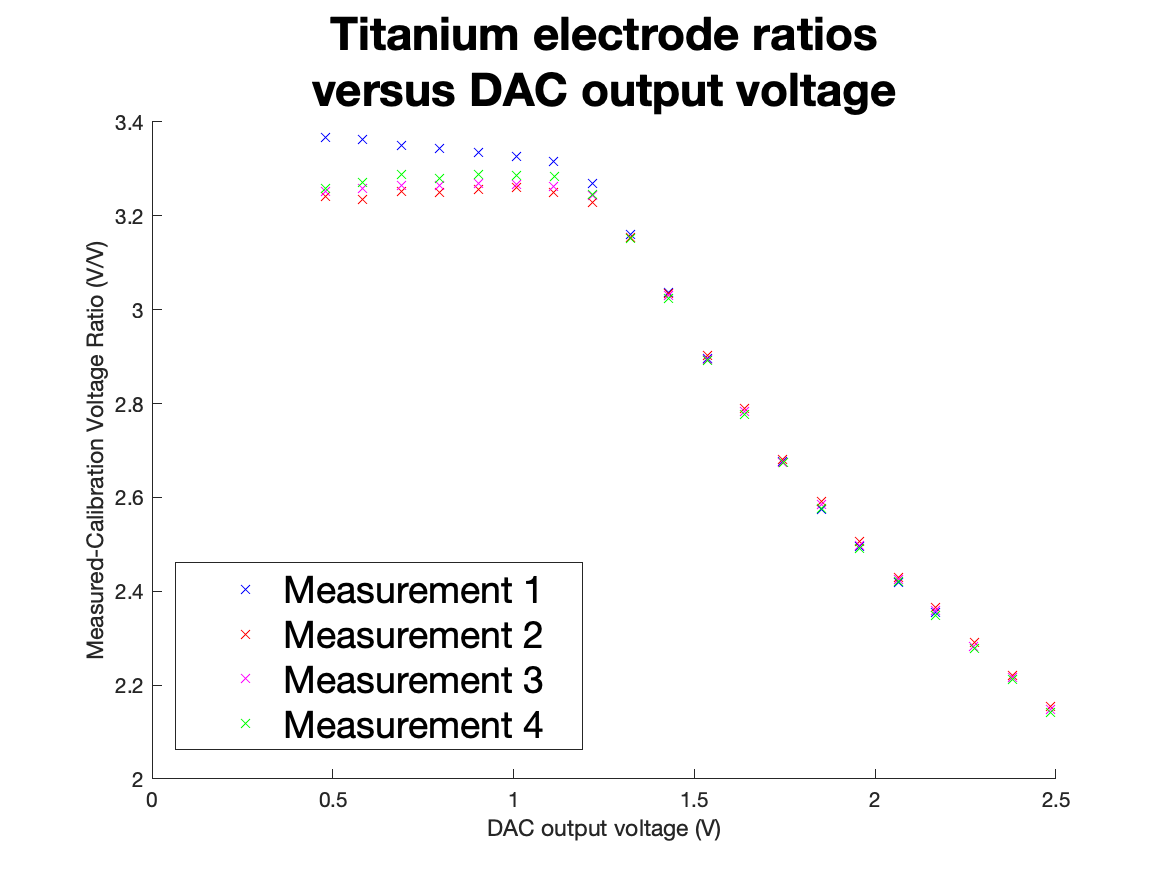
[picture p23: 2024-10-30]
Report/Figures/Testing/Ti18.png

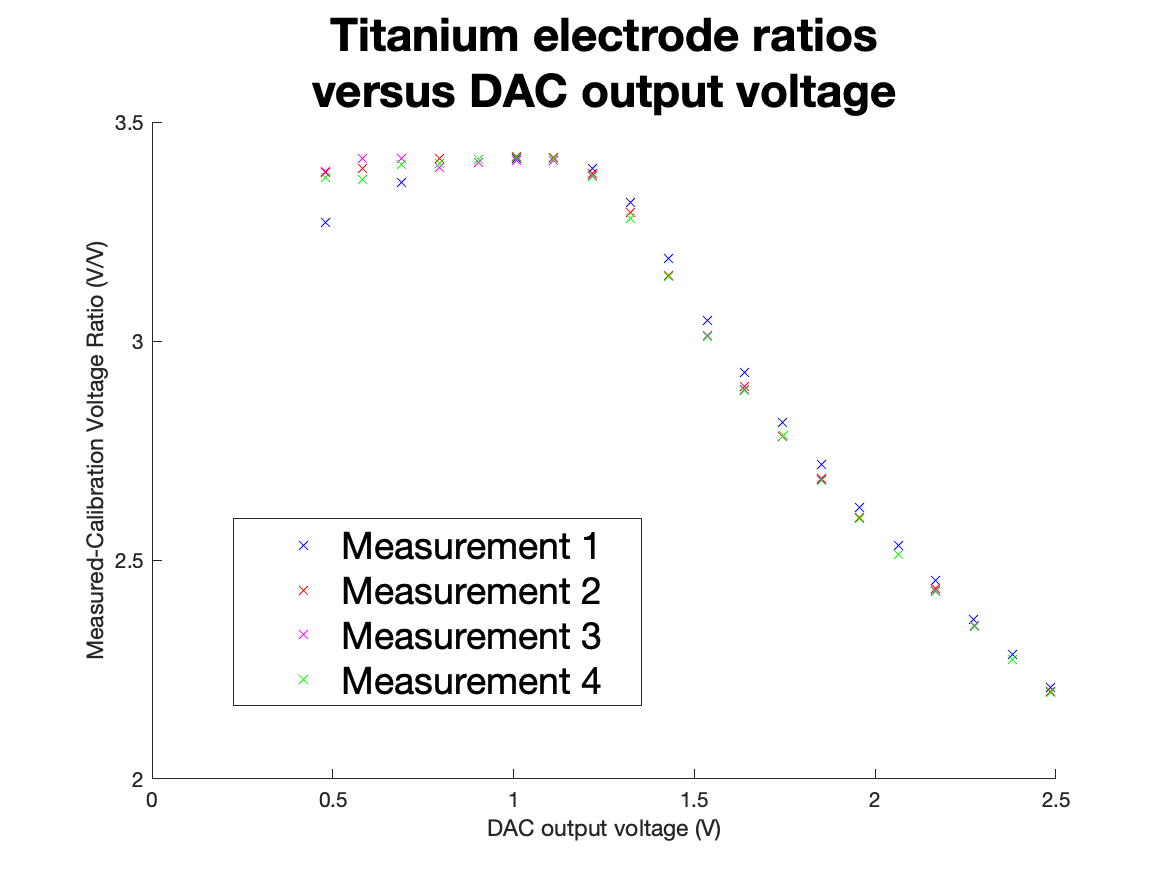
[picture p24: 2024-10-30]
Report/Figures/Testing/Ti17.png

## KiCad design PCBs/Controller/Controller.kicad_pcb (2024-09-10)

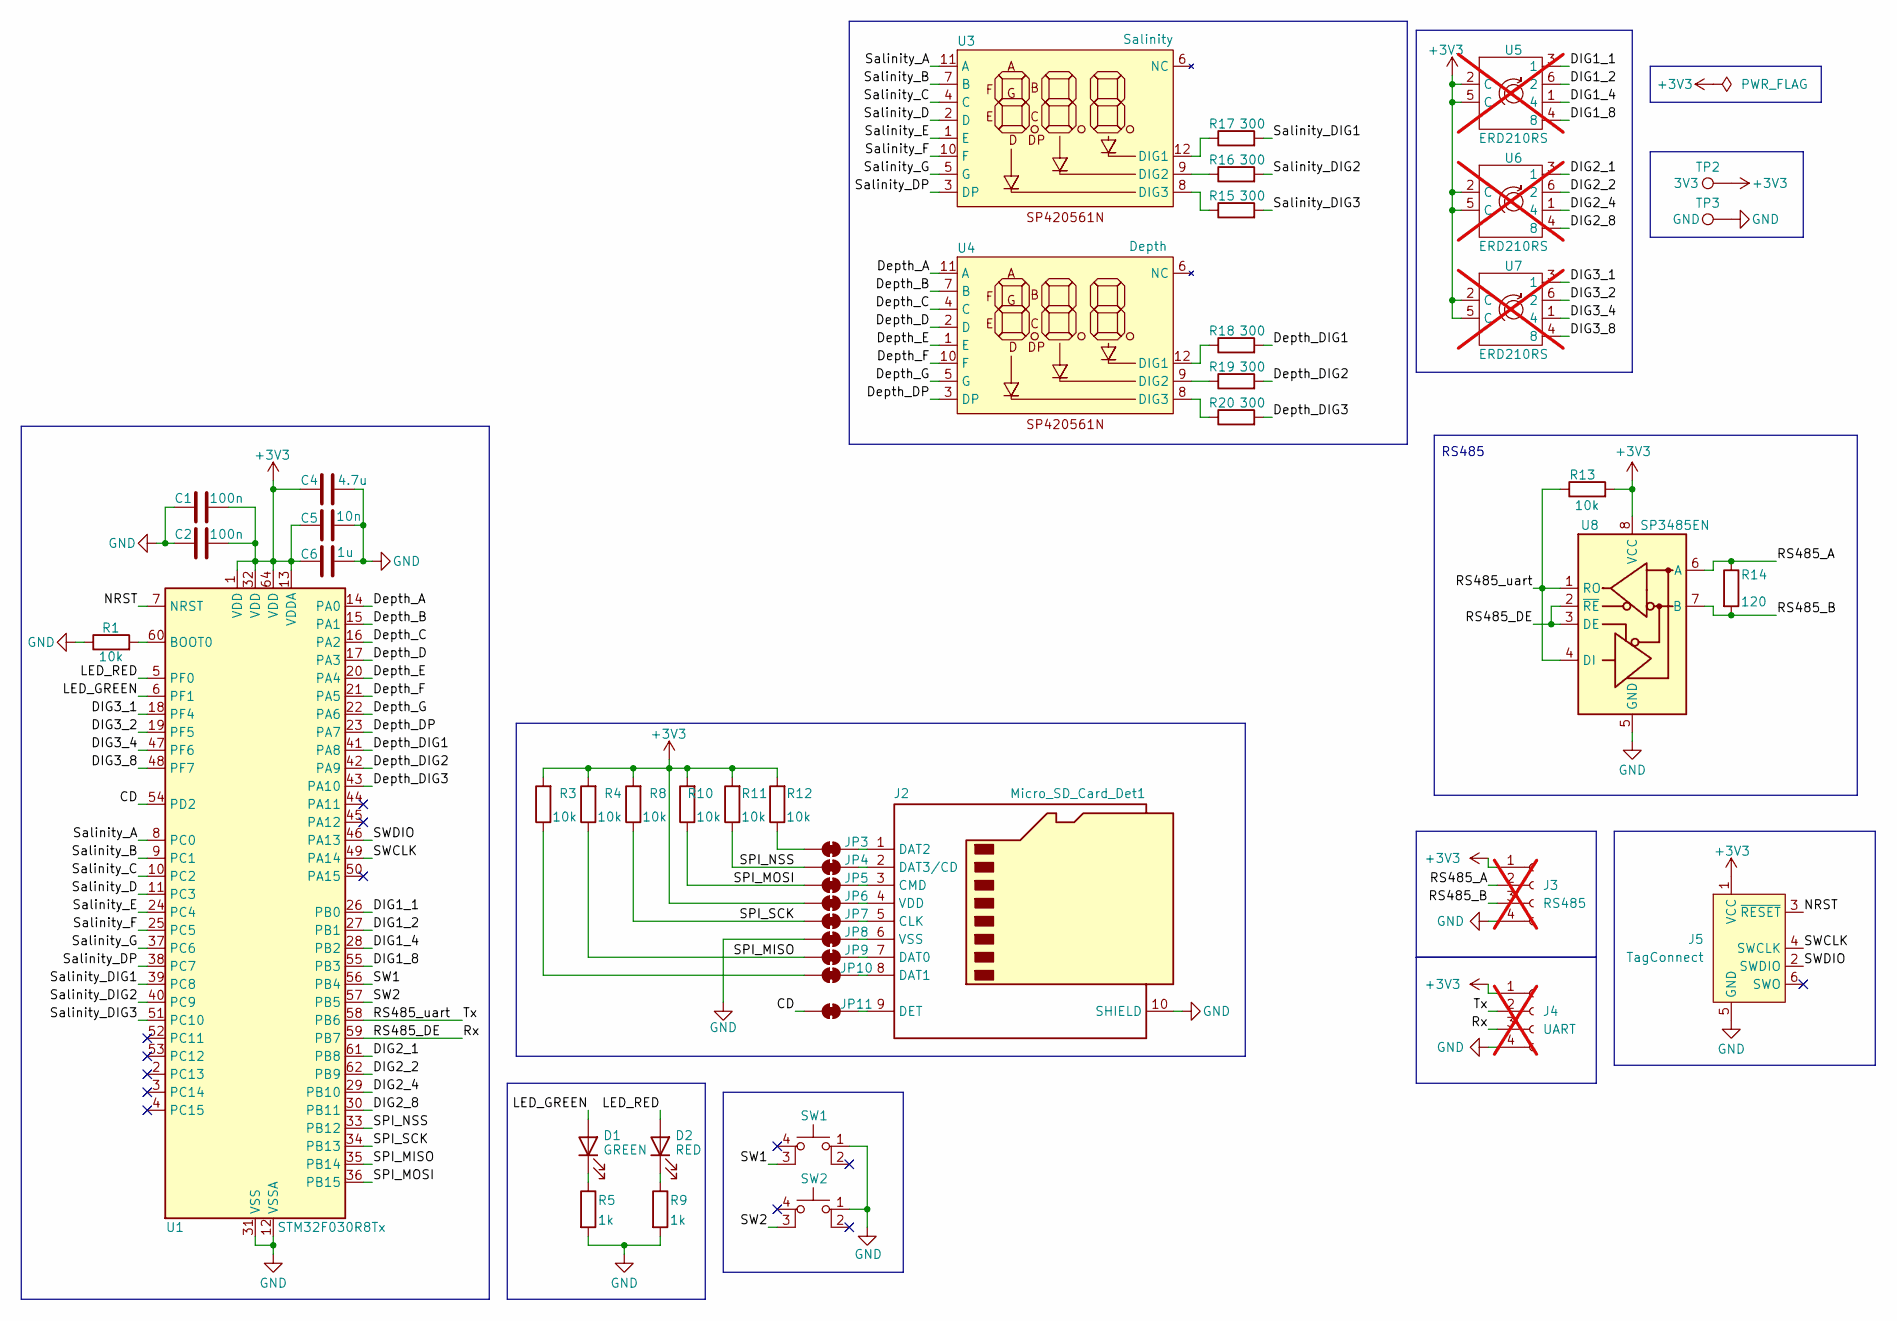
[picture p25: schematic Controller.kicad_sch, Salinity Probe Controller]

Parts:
C1, C2: 100n; C_0603_1608Metric; JLC Part no. C14663
C4: 4.7u; C_0603_1608Metric; JLC Part no. C69182
C5: 10n; C_0603_1608Metric; JLC Part no. C57112
C6: 1u; C_0603_1608Metric; JLC Part no. C15849
D1: GREEN; LED_0805_2012Metric; JLC Part no. C2297
D2: RED; LED_0603_1608Metric; JLC Part no. C2286
J2: Micro_SD_Card_Det1; microSDcard; JLC Part no. C393941
J3: RS485; PinHeader_1x04_P2.54mm_Vertical; not fitted
J4: UART; PinHeader_1x04_P2.54mm_Vertical; not fitted
J5: TagConnect; Tag-Connect_TC2030-IDC-NL_2x03_P1.27mm_Vertical
JP3, JP4, JP5, JP6, JP7, JP8, JP9, JP10, JP11: SolderJumper_2_Bridged; SolderJumper-2_P1.3mm_Bridged_Pad1.0x1.5mm
R1, R3, R4, R8, R10, R11, R12, R13: 10k; R_0603_1608Metric; JLC Part no. C25804
R5, R9: 1k; R_0603_1608Metric; JLC Part no. C21190
R14: 120; R_0603_1608Metric; JLC Part no. C22787
R15, R16, R17, R18, R19, R20: 300; R_1206_3216Metric; JLC Part no. C17887
SW1, SW2: Switch; Push_Button_SPDT; JLC Part no. C318884
TP2: 3V3; TestPoint_THTPad_2.0x2.0mm_Drill1.0mm
TP3: GND; TestPoint_THTPad_2.0x2.0mm_Drill1.0mm
U1: STM32F030R8Tx; LQFP-64_10x10mm_P0.5mm; JLC Part no. C39105
U3: Salinity; SP20561; JLC Part no. C98928
U4: Depth; SP20561; JLC Part no. C98928
U5, U6, U7: ERD210RS; ERD2xxxS; not fitted
U8: SP3485EN; SOIC-8_3.9x4.9mm_P1.27mm; JLC Part no. C8963

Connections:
+3V3: C1.2, C2.2, C4.1, C5.2, C6.2, J3.1, J4.1, J5.1 (VCC), JP6.1 (A), R3.2, R4.2, R8.2, R10.2, R11.2, R12.2, R13.2, TP2.1, U1.1 (VDD), U1.13 (VDDA), U1.32 (VDD), U1.64 (VDD), U5.2 (C), U5.5 (C), U6.2 (C), U6.5 (C), U7.2 (C), U7.5 (C), U8.8 (VCC)
/CD: JP11.1 (A), U1.54 (PD2)
/DIG1_1: U1.26 (PB0), U5.3 (1)
/DIG1_2: U1.27 (PB1), U5.6 (2)
/DIG1_4: U1.28 (PB2), U5.1 (4)
/DIG1_8: U1.55 (PB3), U5.4 (8)
/DIG2_1: U1.61 (PB8), U6.3 (1)
/DIG2_2: U1.62 (PB9), U6.6 (2)
/DIG2_4: U1.29 (PB10), U6.1 (4)
/DIG2_8: U1.30 (PB11), U6.4 (8)
/DIG3_1: U1.18 (PF4), U7.3 (1)
/DIG3_2: U1.19 (PF5), U7.6 (2)
/DIG3_4: U1.47 (PF6), U7.1 (4)
/DIG3_8: U1.48 (PF7), U7.4 (8)
/Depth_A: U1.14 (PA0), U4.11 (A)
/Depth_B: U1.15 (PA1), U4.7 (B)
/Depth_C: U1.16 (PA2), U4.4 (C)
/Depth_D: U1.17 (PA3), U4.2 (D)
/Depth_DIG1: R18.2, U1.41 (PA8)
/Depth_DIG2: R19.2, U1.42 (PA9)
/Depth_DIG3: R20.2, U1.43 (PA10)
/Depth_DP: U1.23 (PA7), U4.3 (DP)
/Depth_E: U1.20 (PA4), U4.1 (E)
/Depth_F: U1.21 (PA5), U4.10 (F)
/Depth_G: U1.22 (PA6), U4.5 (G)
/LED_GREEN: D1.2 (A), U1.6 (PF1)
/LED_RED: D2.2 (A), U1.5 (PF0)
/NRST: J5.3 (~RESET), U1.7 (NRST)
/RS485_A: J3.2, R14.1, U8.6 (A)
/RS485_B: J3.3, R14.2, U8.7 (B)
/RS485_DE: J4.3, U1.59 (PB7), U8.2 (~RE), U8.3 (DE)
/RS485_uart: J4.2, R13.1, U1.58 (PB6), U8.1 (RO), U8.4 (DI)
/SPI_MISO: JP9.1 (A), R4.1, U1.35 (PB14)
/SPI_MOSI: JP5.1 (A), R10.1, U1.36 (PB15)
/SPI_NSS: JP4.1 (A), R11.1, U1.33 (PB12)
/SPI_SCK: JP7.1 (A), R8.1, U1.34 (PB13)
/SW1: SW1.3 (K), U1.56 (PB4)
/SW2: SW2.3 (K), U1.57 (PB5)
/SWCLK: J5.4 (SWCLK), U1.49 (PA14)
/SWDIO: J5.2 (SWDIO), U1.46 (PA13)
/Salinity_A: U1.8 (PC0), U3.11 (A)
/Salinity_B: U1.9 (PC1), U3.7 (B)
/Salinity_C: U1.10 (PC2), U3.4 (C)
/Salinity_D: U1.11 (PC3), U3.2 (D)
/Salinity_DIG1: R17.2, U1.39 (PC8)
/Salinity_DIG2: R16.2, U1.40 (PC9)
/Salinity_DIG3: R15.2, U1.51 (PC10)
/Salinity_DP: U1.38 (PC7), U3.3 (DP)
/Salinity_E: U1.24 (PC4), U3.1 (E)
/Salinity_F: U1.25 (PC5), U3.10 (F)
/Salinity_G: U1.37 (PC6), U3.5 (G)
GND: C1.1, C2.1, C4.2, C5.1, C6.1, J2.10 (SHIELD), J3.4, J4.4, J5.5 (GND), JP8.1 (A), R1.1, R5.2, R9.2, SW1.1, SW2.1, TP3.1, U1.12 (VSSA), U1.31 (VSS), U1.63 (VSS), U8.5 (GND)
unnamed: D1.1 (K), R5.1
unnamed: D2.1 (K), R9.1
unnamed: J2.5 (CLK), JP7.2 (B)
unnamed: J2.3 (CMD), JP5.2 (B)
unnamed: J2.7 (DAT0), JP9.2 (B)
unnamed: J2.8 (DAT1), JP10.2 (B)
unnamed: J2.1 (DAT2), JP3.2 (B)
unnamed: J2.2 (DAT3/CD), JP4.2 (B)
unnamed: J2.9 (DET), JP11.2 (B)
unnamed: J2.4 (VDD), JP6.2 (B)
unnamed: J2.6 (VSS), JP8.2 (B)
unnamed: JP3.1 (A), R12.1
unnamed: JP10.1 (A), R3.1
unnamed: R1.2, U1.60 (BOOT0)
unnamed: R17.1, U3.12 (DIG1)
unnamed: R16.1, U3.9 (DIG2)
unnamed: R15.1, U3.8 (DIG3)
unnamed: R18.1, U4.12 (DIG1)
unnamed: R19.1, U4.9 (DIG2)
unnamed: R20.1, U4.8 (DIG3)

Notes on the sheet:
RS485

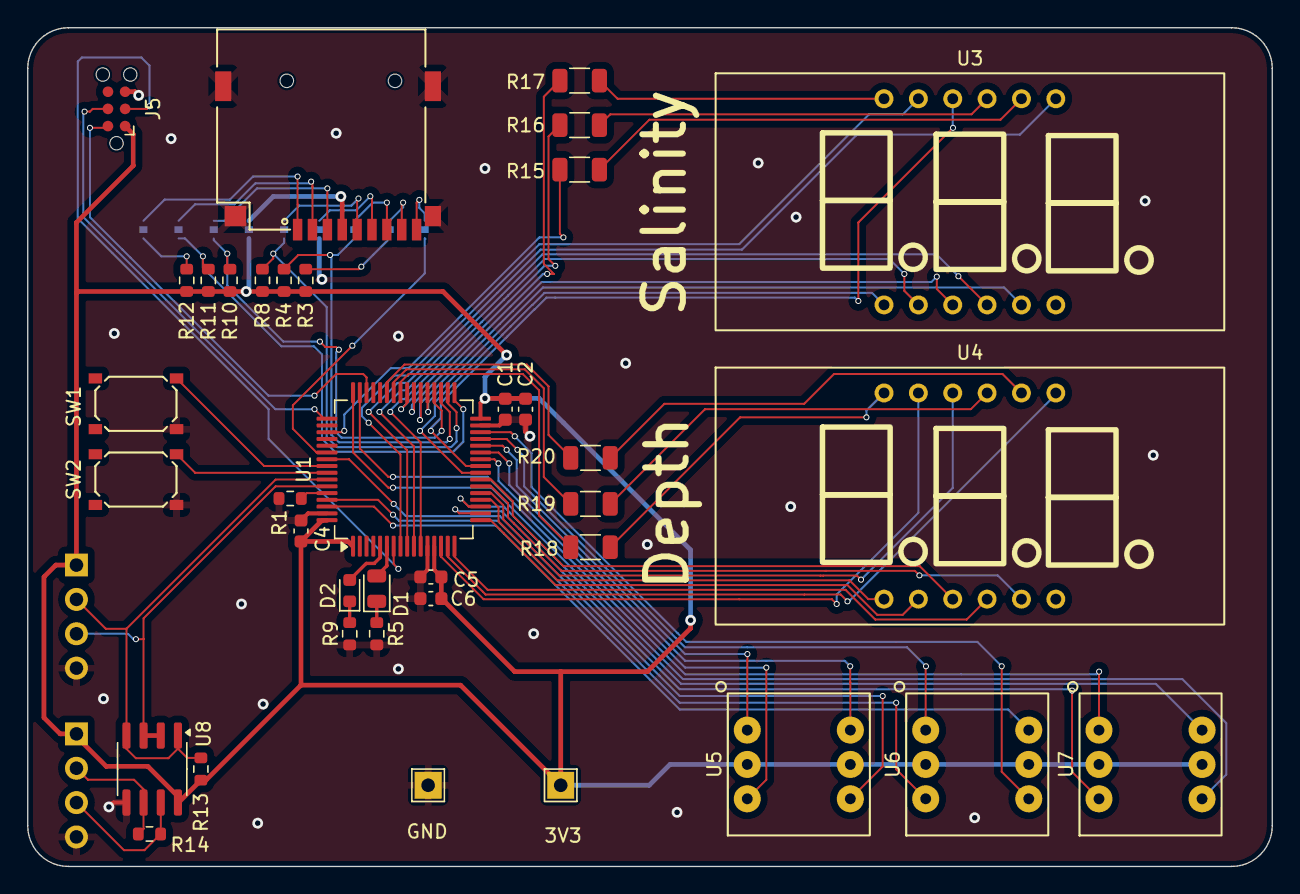
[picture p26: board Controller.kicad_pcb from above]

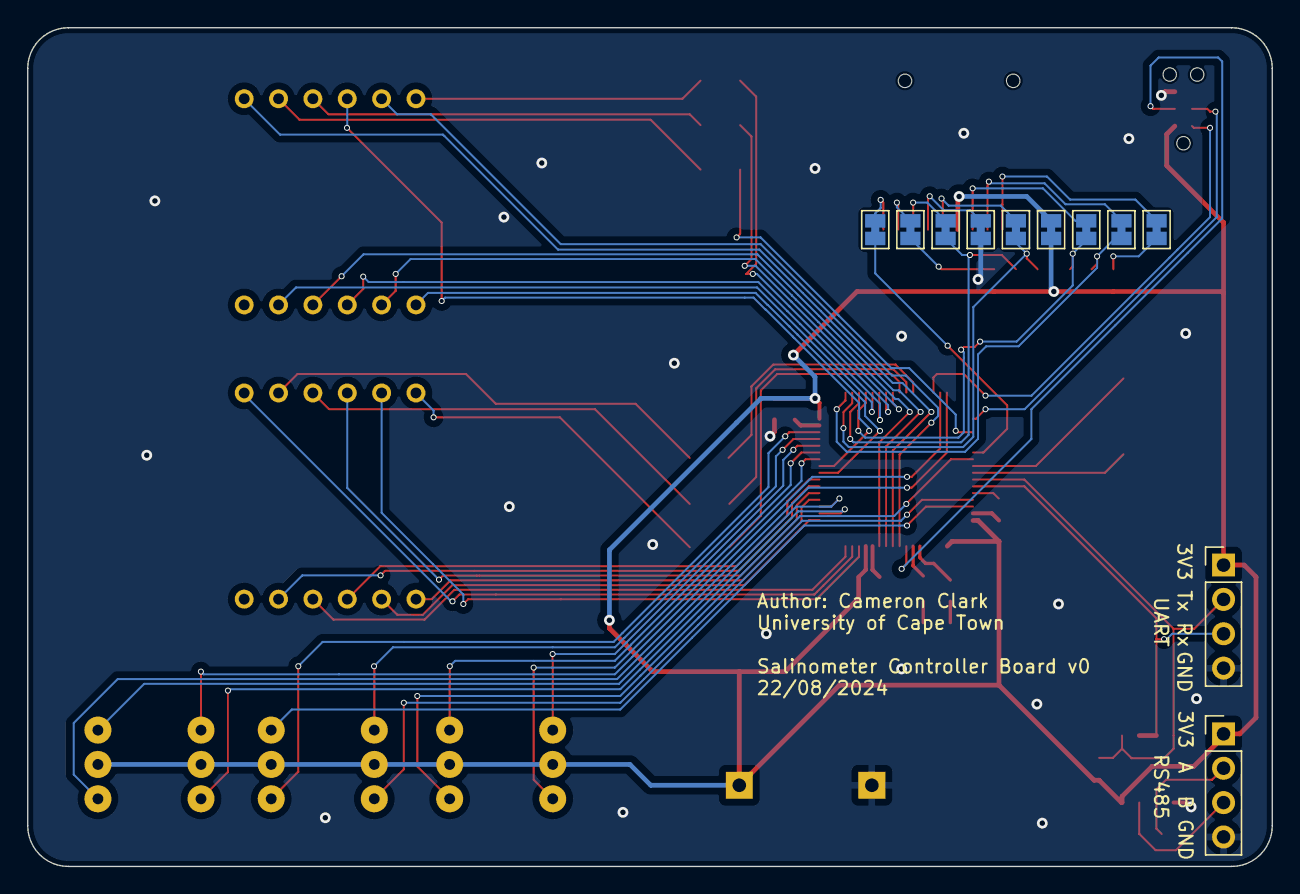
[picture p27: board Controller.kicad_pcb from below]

Board: 2 copper layers, 92.0 x 62.0 mm, 48 parts (11 on the bottom side), 72 nets.

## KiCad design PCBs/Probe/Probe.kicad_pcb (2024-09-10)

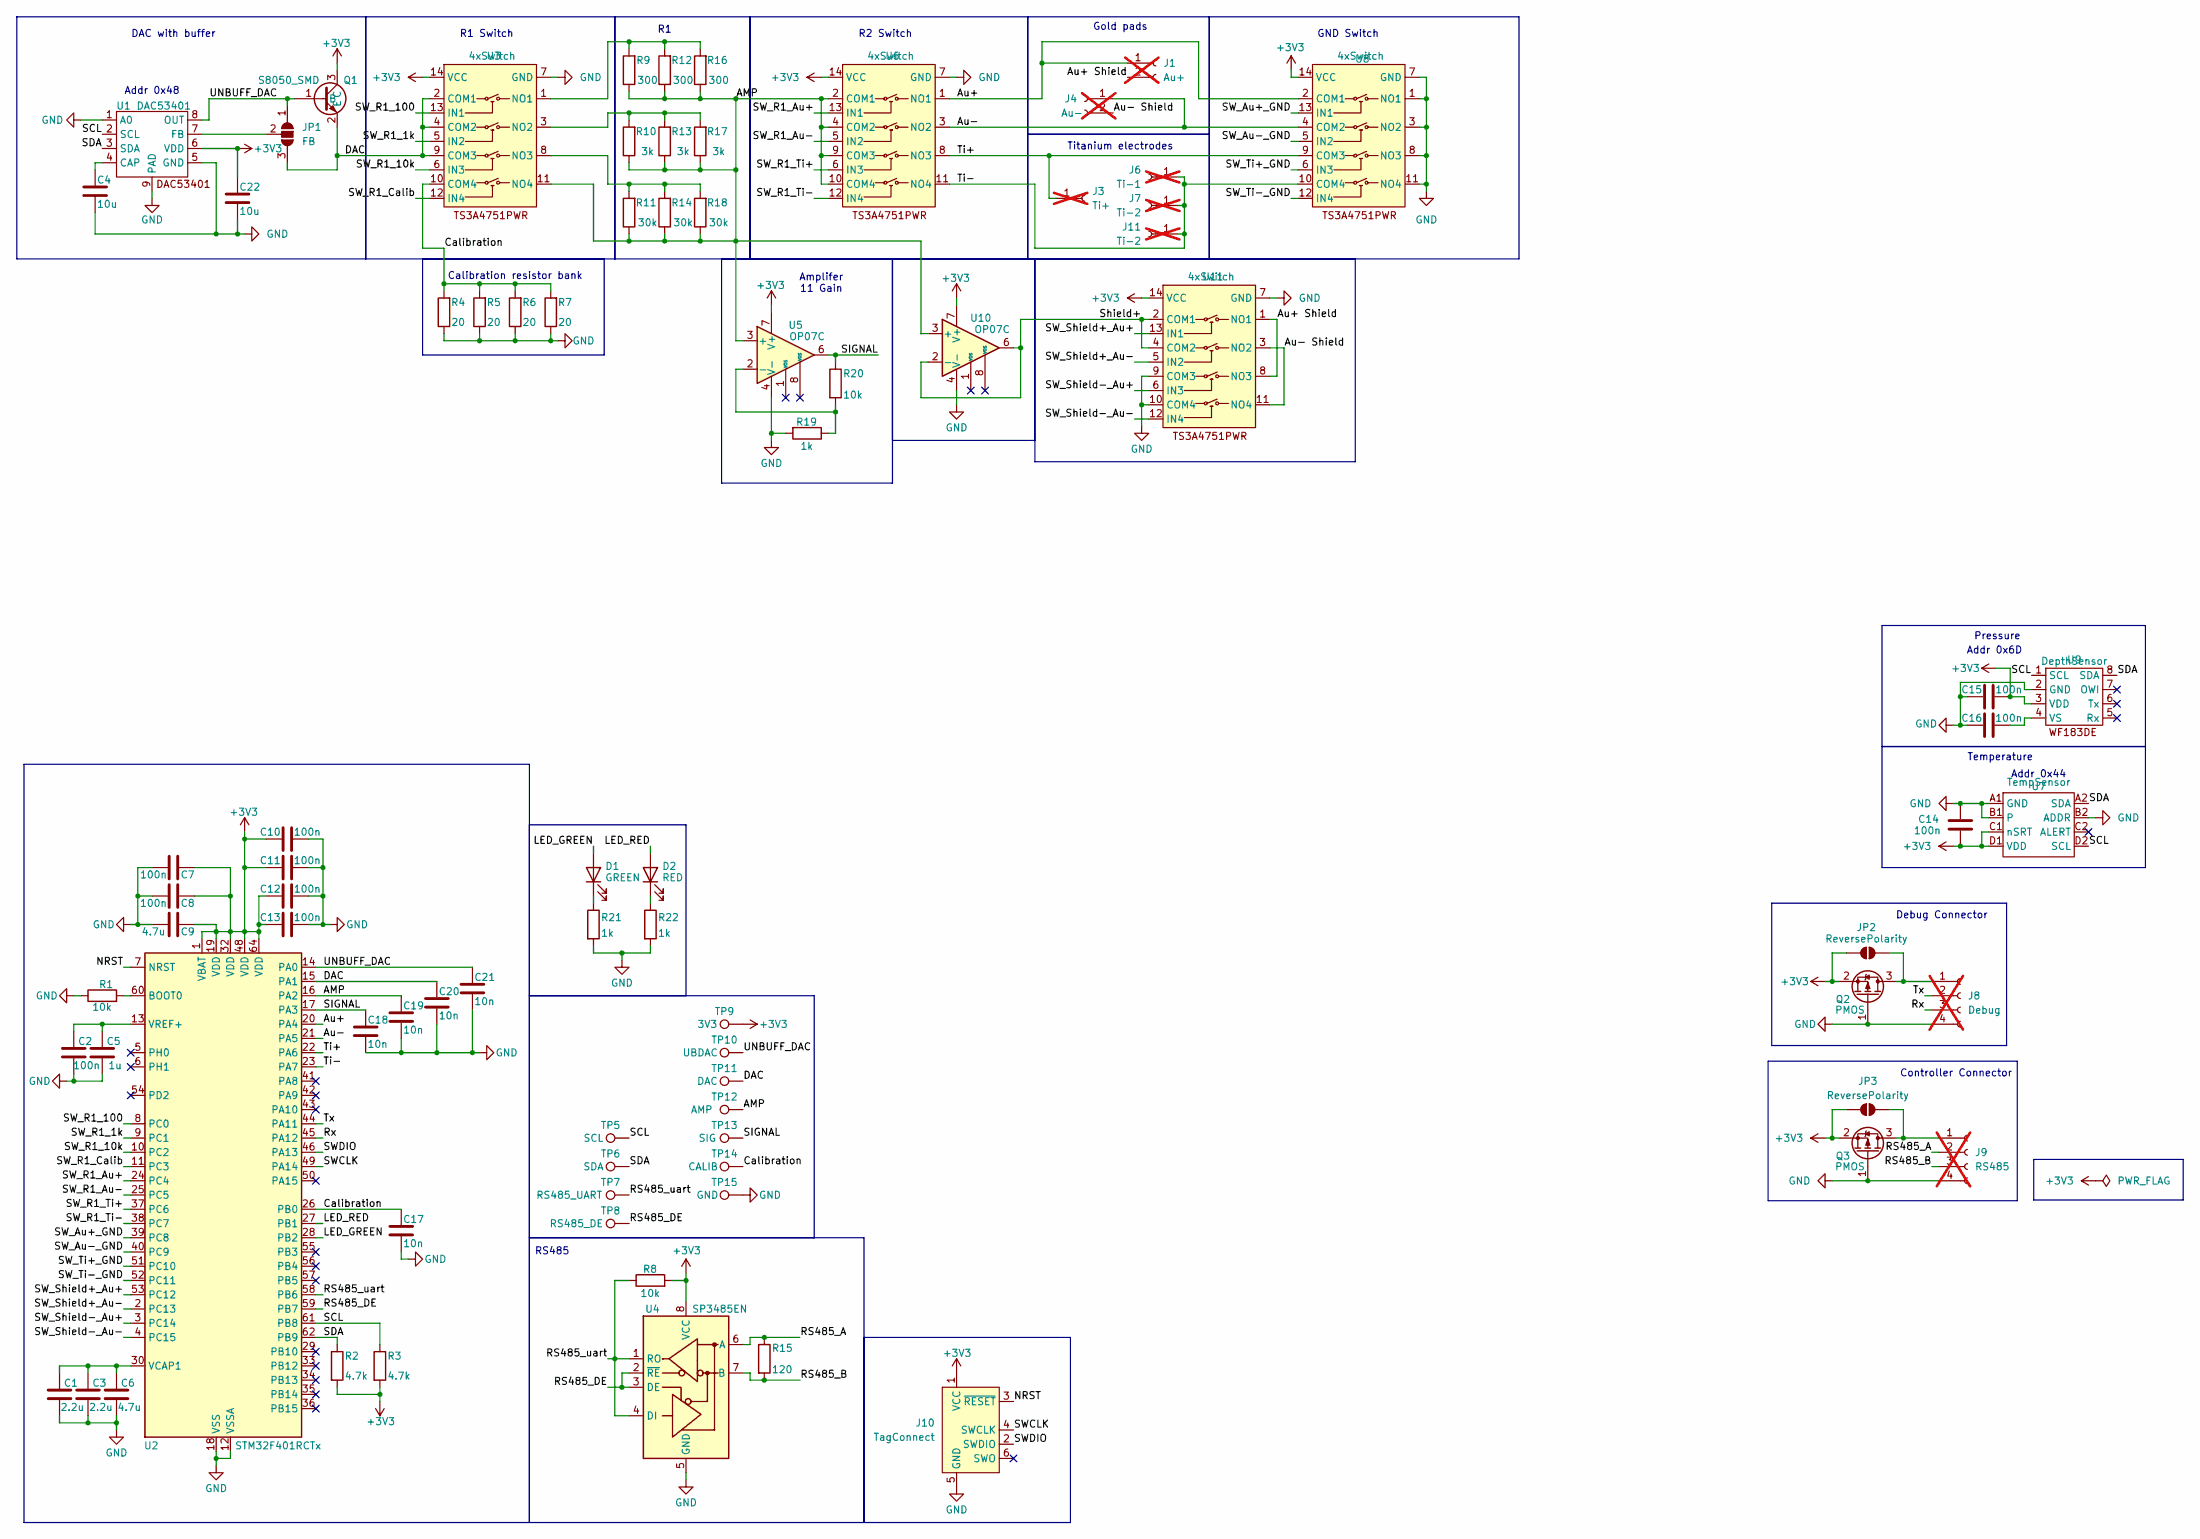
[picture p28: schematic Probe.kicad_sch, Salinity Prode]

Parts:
C1, C3: 2.2u; C_0603_1608Metric; JLC Part no. C23630
C2, C7, C8, C10, C11, C12, C13, C14, C15, C16: 100n; C_0603_1608Metric; JLC Part no. C14663
C4, C22: 10u; C_0603_1608Metric; JLC Part no. C19702
C5: 1u; C_0603_1608Metric; JLC Part no. C15849
C6, C9: 4.7u; C_0603_1608Metric; JLC Part no. C69182
C17, C18, C19, C20, C21: 10n; C_0402_1005Metric; JLC Part no. C15195
D1: GREEN; LED_0805_2012Metric; JLC Part no. C2297
D2: RED; LED_0603_1608Metric; JLC Part no. C2286
J1: Au+; Au_Electrode; not fitted
J3: Ti+; PinHeader_1x01_P2.54mm_Vertical; not fitted
J4: Au-; Au_Electrode; not fitted
J6: Ti-1; PinHeader_1x01_P2.54mm_Vertical; not fitted
J7, J11: Ti-2; PinHeader_1x01_P2.54mm_Vertical; not fitted
J8: Debug; PinSocket_1x04_P2.54mm_Vertical; not fitted
J9: RS485; PinSocket_1x04_P2.54mm_Vertical; not fitted
J10: TagConnect; Tag-Connect_TC2030-IDC-NL_2x03_P1.27mm_Vertical
JP1: FB; SolderJumper-3_P2.0mm_Open_TrianglePad1.0x1.5mm
JP2, JP3: ReversePolarity; SolderJumper-2_P1.3mm_Open_TrianglePad1.0x1.5mm
Q1: S8050_SMD; SOT-23-3; JLC Part no. C2146
Q2, Q3: PMOS; SOT-23; JLC Part no. C15127
R1, R8: 10k; R_0603_1608Metric; JLC Part no. C25804
R2, R3: 4.7k; R_0603_1608Metric; JLC Part no. C23162
R4, R5, R6, R7: 20; R_0603_1608Metric; JLC Part no. C22950
R9, R12, R16: 300; R_0603_1608Metric; JLC Part no. C23025
R10, R13, R17: 3k; R_0603_1608Metric; JLC Part no. C4211
R11, R14, R18: 30k; R_0603_1608Metric; JLC Part no. C22984
R15: 120; R_0603_1608Metric; JLC Part no. C22787
R19: 1k; R_1206_3216Metric; JLC Part no. C4410
R20: 10k; R_1206_3216Metric; JLC Part no. C17902
R21, R22: 1k; R_0603_1608Metric; JLC Part no. C21190
TP5: SCL; TestPoint_THTPad_2.0x2.0mm_Drill1.0mm
TP6: SDA; TestPoint_THTPad_2.0x2.0mm_Drill1.0mm
TP7: RS485_UART; TestPoint_THTPad_2.0x2.0mm_Drill1.0mm
TP8: RS485_DE; TestPoint_THTPad_2.0x2.0mm_Drill1.0mm
TP9: 3V3; TestPoint_THTPad_2.0x2.0mm_Drill1.0mm
TP10: UBDAC; TestPoint_THTPad_2.0x2.0mm_Drill1.0mm
TP11: DAC; TestPoint_THTPad_2.0x2.0mm_Drill1.0mm
TP12: AMP; TestPoint_THTPad_2.0x2.0mm_Drill1.0mm
TP13: SIG; TestPoint_THTPad_2.0x2.0mm_Drill1.0mm
TP14: CALIB; TestPoint_THTPad_2.0x2.0mm_Drill1.0mm
TP15: GND; TestPoint_THTPad_2.0x2.0mm_Drill1.0mm
U1: DAC53401; WSON-8-1EP_2x2mm_P0.5mm_EP0.9x1.6mm; JLC Part no. C2861165
U2: STM32F401RCTx; LQFP-64_10x10mm_P0.5mm; JLC Part no. C1339473
U3, U6, U8, U11: 4xSwitch; TSSOP-14_4.4x5mm_P0.65mm; JLC Part no. C128399
U4: SP3485EN; SOIC-8_3.9x4.9mm_P1.27mm; JLC Part no. C8963
U5, U10: OP07C; SOIC-8_3.9x4.9mm_P1.27mm; JLC Part no. C7433
U7: TempSensor; WLCSP-8_1.551x2.284mm_P0.5mm; JLC Part no. C2758003
U9: DepthSensor; WF183DE; JLC Part no. C20415992

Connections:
+3V3: C7.1, C8.1, C9.1, C10.1, C11.1, C12.1, C13.1, C14.2, C15.2, C22.1, J10.1 (VCC), JP2.1 (A), JP3.1 (A), Q1.3 (C), Q2.2 (S), Q3.2 (S), R2.2, R3.2, R8.2, TP9.1, U1.6 (VDD), U2.1 (VBAT), U2.19 (VDD), U2.32 (VDD), U2.48 (VDD), U2.64 (VDD), U3.14 (VCC), U4.8 (VCC), U5.7 (V+), U6.14 (VCC), U7.C1 (nSRT), U7.D1 (VDD), U8.14 (VCC), U9.3 (VDD), U10.7 (V+), U11.14 (VCC)
/AMP: C19.1, R9.1, R10.1, R11.1, R12.1, R13.1, R14.1, R16.1, R17.1, R18.1, TP12.1, U2.16 (PA2), U3.11 (NO4), U5.3 (+), U6.2 (COM1), U6.4 (COM2), U6.9 (COM3), U6.10 (COM4), U10.3 (+)
/Au+: J1.1, U2.20 (PA4), U6.1 (NO1), U8.2 (COM1)
/Au+ Shield: J1.2, U11.1 (NO1), U11.8 (NO3)
/Au-: J4.1, U2.21 (PA5), U6.3 (NO2), U8.4 (COM2)
/Au- Shield: J4.2, U11.3 (NO2), U11.11 (NO4)
/Calibration: C17.1, R4.2, R5.2, R6.2, R7.2, TP14.1, U2.26 (PB0), U3.10 (COM4)
/DAC: C20.1, JP1.3 (B), Q1.2 (E), TP11.1, U2.15 (PA1), U3.2 (COM1), U3.4 (COM2), U3.9 (COM3)
/LED_GREEN: D1.2 (A), U2.28 (PB2)
/LED_RED: D2.2 (A), U2.27 (PB1)
/NRST: J10.3 (~RESET), U2.7 (NRST)
/RS485_A: J9.2, R15.1, U4.6 (A)
/RS485_B: J9.3, R15.2, U4.7 (B)
/RS485_DE: TP8.1, U2.59 (PB7), U4.2 (~RE), U4.3 (DE)
/RS485_uart: R8.1, TP7.1, U2.58 (PB6), U4.1 (RO), U4.4 (DI)
/Rx: J8.3, U2.45 (PA12)
/SCL: R3.1, TP5.1, U1.2 (SCL), U2.61 (PB8), U7.D2 (SCL), U9.1 (SCL)
/SDA: R2.1, TP6.1, U1.3 (SDA), U2.62 (PB9), U7.A2 (SDA), U9.8 (SDA)
/SIGNAL: C18.1, R20.1, TP13.1, U2.17 (PA3), U5.6
/SWCLK: J10.4 (SWCLK), U2.49 (PA14)
/SWDIO: J10.2 (SWDIO), U2.46 (PA13)
/SW_Au+_GND: U2.39 (PC8), U8.13 (IN1)
/SW_Au-_GND: U2.40 (PC9), U8.5 (IN2)
/SW_R1_1k: U2.9 (PC1), U3.5 (IN2)
/SW_R1_10k: U2.10 (PC2), U3.6 (IN3)
/SW_R1_100: U2.8 (PC0), U3.13 (IN1)
/SW_R1_Au+: U2.24 (PC4), U6.13 (IN1)
/SW_R1_Au-: U2.25 (PC5), U6.5 (IN2)
/SW_R1_Calib: U2.11 (PC3), U3.12 (IN4)
/SW_R1_Ti+: U2.37 (PC6), U6.6 (IN3)
/SW_R1_Ti-: U2.38 (PC7), U6.12 (IN4)
/SW_Shield+_Au+: U2.53 (PC12), U11.13 (IN1)
/SW_Shield+_Au-: U2.2 (PC13), U11.5 (IN2)
/SW_Shield-_Au+: U2.3 (PC14), U11.6 (IN3)
/SW_Shield-_Au-: U2.4 (PC15), U11.12 (IN4)
/SW_Ti+_GND: U2.51 (PC10), U8.6 (IN3)
/SW_Ti-_GND: U2.52 (PC11), U8.12 (IN4)
/Shield+: U10.2 (-), U10.6, U11.2 (COM1), U11.4 (COM2)
/Ti+: J3.1, U2.22 (PA6), U6.8 (NO3), U8.9 (COM3)
/Ti-: J6.1, J7.1, J11.1, U2.23 (PA7), U6.11 (NO4), U8.10 (COM4)
/Tx: J8.2, U2.44 (PA11)
/UNBUFF_DAC: C21.1, JP1.1 (A), Q1.1 (B), TP10.1, U1.8 (OUT), U2.14 (PA0)
GND: C1.1, C2.1, C3.1, C4.2, C5.1, C6.1, C7.2, C8.2, C9.2, C10.2, C11.2, C12.2, C13.2, C14.1, C15.1, C16.1, C17.2, C18.2, C19.2, C20.2, C21.2, C22.2, J8.4, J9.4, J10.5 (GND), Q2.1 (G), Q3.1 (G), R1.1, R4.1, R5.1, R6.1, R7.1, R19.2, R21.2, R22.2, TP15.1, U1.1 (A0), U1.5 (GND), U1.9 (PAD), U2.12 (VSSA), U2.18 (VSS), U2.31 (VSS), U2.47 (VSS), U2.63 (VSS), U3.7 (GND), U4.5 (GND), U5.4 (V-), U6.7 (GND), U7.A1 (GND), U7.B1, U7.B2 (ADDR), U8.1 (NO1), U8.3 (NO2), U8.7 (GND), U8.8 (NO3), U8.11 (NO4), U9.2 (GND), U10.4 (V-), U11.7 (GND), U11.9 (COM3), U11.10 (COM4)
unnamed: D1.1 (K), R21.1
unnamed: D2.1 (K), R22.1
unnamed: J8.1, JP2.2 (B), Q2.3 (D)
unnamed: J9.1, JP3.2 (B), Q3.3 (D)
unnamed: JP1.2 (C), U1.7 (FB)
unnamed: C4.1, U1.4 (CAP)
unnamed: R1.2, U2.60 (BOOT0)
unnamed: C1.2, C3.2, C6.2, U2.30 (VCAP1)
unnamed: C2.2, C5.2, U2.13 (VREF+)
unnamed: R9.2, R12.2, R16.2, U3.1 (NO1)
unnamed: R10.2, R13.2, R17.2, U3.3 (NO2)
unnamed: R11.2, R14.2, R18.2, U3.8 (NO3)
unnamed: R19.1, R20.2, U5.2 (-)
unnamed: C16.2, U9.4 (VS)

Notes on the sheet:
R1 Switch
Gold pads
GND Switch
Debug Connector
Pressure
Addr 0x48
RS485
DAC with buffer
Addr 0x44
Calibration resistor bank
Controller Connector
Titanium electrodes
R2 Switch
Amplifer 11 Gain
Addr 0x6D
Temperature

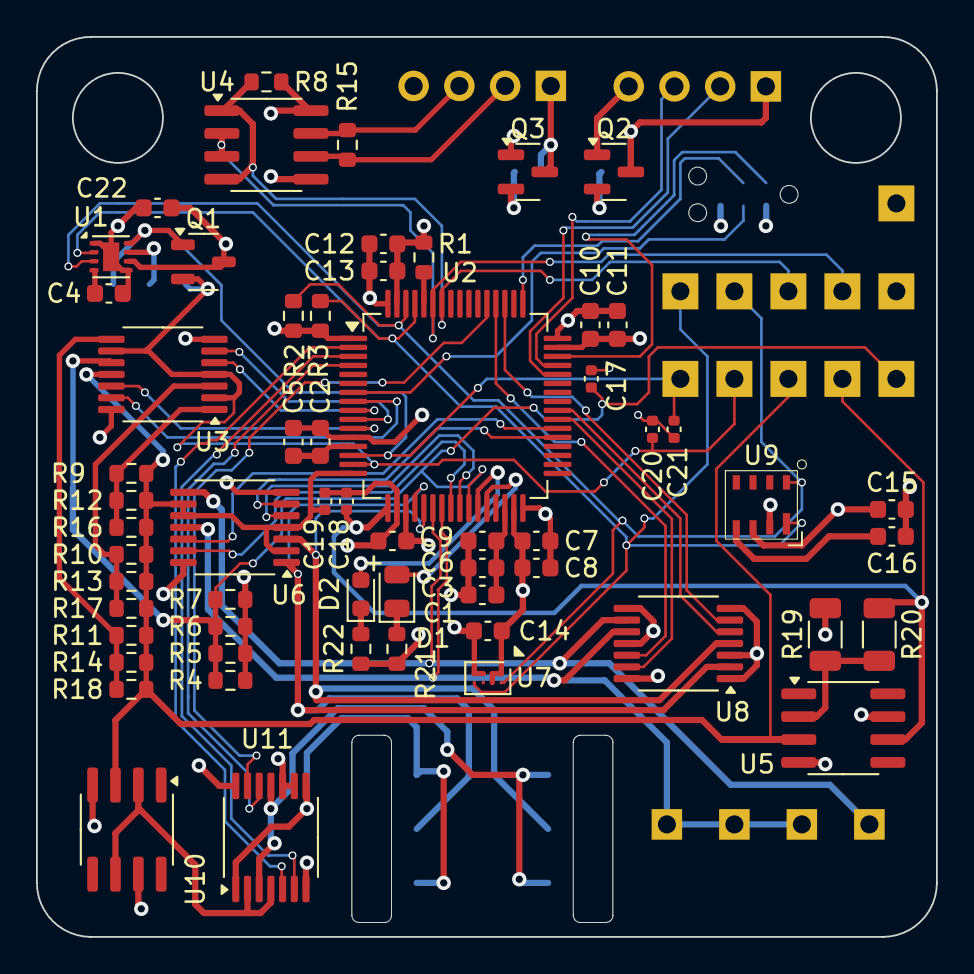
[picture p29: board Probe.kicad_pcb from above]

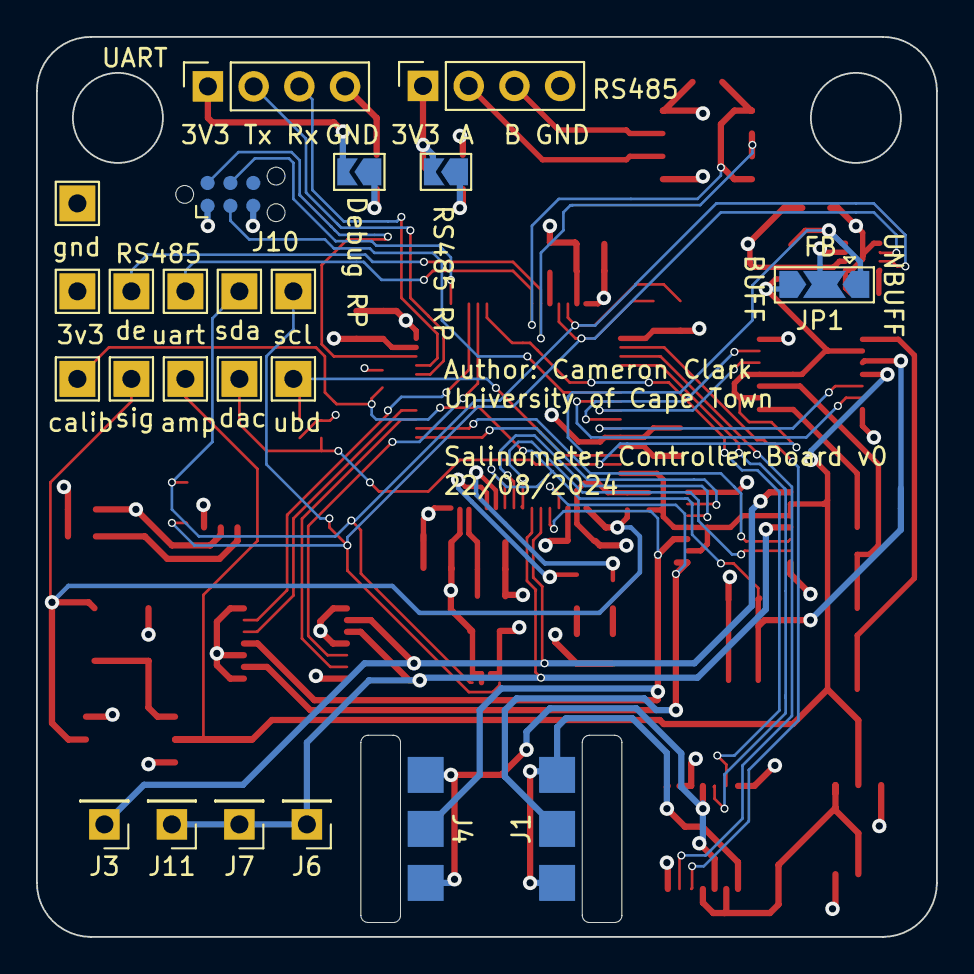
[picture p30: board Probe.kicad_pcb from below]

Board: 4 copper layers, 50.0 x 50.0 mm, 83 parts (23 on the bottom side), 57 nets.

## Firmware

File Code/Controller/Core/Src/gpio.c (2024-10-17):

/* USER CODE BEGIN Header */
/**
  ******************************************************************************
  * @file    gpio.c
  * @brief   This file provides code for the configuration
  *          of all used GPIO pins.
  ******************************************************************************
  * @attention
  *
  * Copyright (c) 2024 STMicroelectronics.
  * All rights reserved.
  *
  * This software is licensed under terms that can be found in the LICENSE file
  * in the root directory of this software component.
  * If no LICENSE file comes with this software, it is provided AS-IS.
  *
  ******************************************************************************
  */
/* USER CODE END Header */

/* Includes ------------------------------------------------------------------*/
#include "gpio.h"

/* USER CODE BEGIN 0 */

/* USER CODE END 0 */

/*----------------------------------------------------------------------------*/
/* Configure GPIO                                                             */
/*----------------------------------------------------------------------------*/
/* USER CODE BEGIN 1 */

/* USER CODE END 1 */

/** Configure pins as
        * Analog
        * Input
        * Output
        * EVENT_OUT
        * EXTI
        * Free pins are configured automatically as Analog (this feature is enabled through
        * the Code Generation settings)
*/
void MX_GPIO_Init(void)
{

  GPIO_InitTypeDef GPIO_InitStruct = {0};

  /* GPIO Ports Clock Enable */
  __HAL_RCC_GPIOC_CLK_ENABLE();
  __HAL_RCC_GPIOF_CLK_ENABLE();
  __HAL_RCC_GPIOA_CLK_ENABLE();
  __HAL_RCC_GPIOB_CLK_ENABLE();
  __HAL_RCC_GPIOD_CLK_ENABLE();

  /*Configure GPIO pin Output Level */
  HAL_GPIO_WritePin(GPIOF, LED_Red_Pin|LED_Green_Pin, GPIO_PIN_RESET);

  /*Configure GPIO pin Output Level */
  HAL_GPIO_WritePin(GPIOC, Salinity_A_Pin|Salinity_B_Pin|Salinity_C_Pin|Salinity_D_Pin
                          |Salinity_E_Pin|Salinity_F_Pin|Salinity_G_Pin|Salinity_DP_Pin
                          |Salinity_DIG1_Pin|Salinity_DIG2_Pin|Salinity_DIG3_Pin, GPIO_PIN_RESET);

  /*Configure GPIO pin Output Level */
  HAL_GPIO_WritePin(GPIOA, Depth_A_Pin|Depth_B_Pin|Depth_C_Pin|Depth_D_Pin
                          |Depth_E_Pin|Depth_F_Pin|Depth_G_Pin|Depth_DP_Pin
                          |Depth_DIG1_Pin|Depth_DIG2_Pin|Depth_DIG3_Pin, GPIO_PIN_RESET);

  /*Configure GPIO pin Output Level */
  HAL_GPIO_WritePin(GPIOB, SPI_NSS_Pin|RS485_DE_Pin, GPIO_PIN_RESET);

  /*Configure GPIO pins : PC13 PC14 PC15 PC11
                           PC12 */
  GPIO_InitStruct.Pin = GPIO_PIN_13|GPIO_PIN_14|GPIO_PIN_15|GPIO_PIN_11
                          |GPIO_PIN_12;
  GPIO_InitStruct.Mode = GPIO_MODE_ANALOG;
  GPIO_InitStruct.Pull = GPIO_NOPULL;
  HAL_GPIO_Init(GPIOC, &GPIO_InitStruct);

  /*Configure GPIO pins : PFPin PFPin */
  GPIO_InitStruct.Pin = LED_Red_Pin|LED_Green_Pin;
  GPIO_InitStruct.Mode = GPIO_MODE_OUTPUT_PP;
  GPIO_InitStruct.Pull = GPIO_NOPULL;
  GPIO_InitStruct.Speed = GPIO_SPEED_FREQ_LOW;
  HAL_GPIO_Init(GPIOF, &GPIO_InitStruct);

  /*Configure GPIO pins : PCPin PCPin PCPin PCPin
                           PCPin PCPin PCPin PCPin */
  GPIO_InitStruct.Pin = Salinity_A_Pin|Salinity_B_Pin|Salinity_C_Pin|Salinity_D_Pin
                          |Salinity_E_Pin|Salinity_F_Pin|Salinity_G_Pin|Salinity_DP_Pin;
  GPIO_InitStruct.Mode = GPIO_MODE_OUTPUT_PP;
  GPIO_InitStruct.Pull = GPIO_NOPULL;
  GPIO_InitStruct.Speed = GPIO_SPEED_FREQ_LOW;
  HAL_GPIO_Init(GPIOC, &GPIO_InitStruct);

  /*Configure GPIO pins : PAPin PAPin PAPin PAPin
                           PAPin PAPin PAPin PAPin */
  GPIO_InitStruct.Pin = Depth_A_Pin|Depth_B_Pin|Depth_C_Pin|Depth_D_Pin
                          |Depth_E_Pin|Depth_F_Pin|Depth_G_Pin|Depth_DP_Pin;
  GPIO_InitStruct.Mode = GPIO_MODE_OUTPUT_PP;
  GPIO_InitStruct.Pull = GPIO_NOPULL;
  GPIO_InitStruct.Speed = GPIO_SPEED_FREQ_LOW;
  HAL_GPIO_Init(GPIOA, &GPIO_InitStruct);

  /*Configure GPIO pins : PFPin PFPin PFPin */
  GPIO_InitStruct.Pin = DIG3_4_Pin|DIG3_8_Pin|DIG3_2_Pin;
  GPIO_InitStruct.Mode = GPIO_MODE_INPUT;
  GPIO_InitStruct.Pull = GPIO_PULLDOWN;
  HAL_GPIO_Init(GPIOF, &GPIO_InitStruct);

  /*Configure GPIO pins : PBPin PBPin PBPin PBPin
                           PBPin PBPin */
  GPIO_InitStruct.Pin = DIG1_4_Pin|DIG1_8_Pin|DIG2_2_Pin|DIG1_2_Pin
                          |DIG2_4_Pin|DIG2_8_Pin;
  GPIO_InitStruct.Mode = GPIO_MODE_INPUT;
  GPIO_InitStruct.Pull = GPIO_PULLDOWN;
  HAL_GPIO_Init(GPIOB, &GPIO_InitStruct);

  /*Configure GPIO pins : PBPin PBPin */
  GPIO_InitStruct.Pin = DIG1_1_Pin|DIG2_1_Pin;
  GPIO_InitStruct.Mode = GPIO_MODE_IT_RISING_FALLING;
  GPIO_InitStruct.Pull = GPIO_PULLDOWN;
  HAL_GPIO_Init(GPIOB, &GPIO_InitStruct);

  /*Configure GPIO pin : PtPin */
  GPIO_InitStruct.Pin = SPI_NSS_Pin;
  GPIO_InitStruct.Mode = GPIO_MODE_OUTPUT_OD;
  GPIO_InitStruct.Pull = GPIO_NOPULL;
  GPIO_InitStruct.Speed = GPIO_SPEED_FREQ_LOW;
  HAL_GPIO_Init(SPI_NSS_GPIO_Port, &GPIO_InitStruct);

  /*Configure GPIO pins : PCPin PCPin PCPin */
  GPIO_InitStruct.Pin = Salinity_DIG1_Pin|Salinity_DIG2_Pin|Salinity_DIG3_Pin;
  GPIO_InitStruct.Mode = GPIO_MODE_OUTPUT_OD;
  GPIO_InitStruct.Pull = GPIO_NOPULL;
  GPIO_InitStruct.Speed = GPIO_SPEED_FREQ_LOW;
  HAL_GPIO_Init(GPIOC, &GPIO_InitStruct);

  /*Configure GPIO pins : PAPin PAPin PAPin */
  GPIO_InitStruct.Pin = Depth_DIG1_Pin|Depth_DIG2_Pin|Depth_DIG3_Pin;
  GPIO_InitStruct.Mode = GPIO_MODE_OUTPUT_OD;
  GPIO_InitStruct.Pull = GPIO_NOPULL;
  GPIO_InitStruct.Speed = GPIO_SPEED_FREQ_LOW;
  HAL_GPIO_Init(GPIOA, &GPIO_InitStruct);

  /*Configure GPIO pins : PA11 PA12 PA15 */
  GPIO_InitStruct.Pin = GPIO_PIN_11|GPIO_PIN_12|GPIO_PIN_15;
  GPIO_InitStruct.Mode = GPIO_MODE_ANALOG;
  GPIO_InitStruct.Pull = GPIO_NOPULL;
  HAL_GPIO_Init(GPIOA, &GPIO_InitStruct);

  /*Configure GPIO pin : PtPin */
  GPIO_InitStruct.Pin = DIG3_1_Pin;
  GPIO_InitStruct.Mode = GPIO_MODE_IT_RISING_FALLING;
  GPIO_InitStruct.Pull = GPIO_PULLDOWN;
  HAL_GPIO_Init(DIG3_1_GPIO_Port, &GPIO_InitStruct);

  /*Configure GPIO pin : PD2 */
  GPIO_InitStruct.Pin = GPIO_PIN_2;
  GPIO_InitStruct.Mode = GPIO_MODE_ANALOG;
  GPIO_InitStruct.Pull = GPIO_NOPULL;
  HAL_GPIO_Init(GPIOD, &GPIO_InitStruct);

  /*Configure GPIO pins : PBPin PBPin */
  GPIO_InitStruct.Pin = SW1_Pin|SW2_Pin;
  GPIO_InitStruct.Mode = GPIO_MODE_IT_FALLING;
  GPIO_InitStruct.Pull = GPIO_PULLUP;
  HAL_GPIO_Init(GPIOB, &GPIO_InitStruct);

  /*Configure GPIO pin : PtPin */
  GPIO_InitStruct.Pin = RS485_DE_Pin;
  GPIO_InitStruct.Mode = GPIO_MODE_OUTPUT_PP;
  GPIO_InitStruct.Pull = GPIO_NOPULL;
  GPIO_InitStruct.Speed = GPIO_SPEED_FREQ_LOW;
  HAL_GPIO_Init(RS485_DE_GPIO_Port, &GPIO_InitStruct);

  /* EXTI interrupt init*/
  HAL_NVIC_SetPriority(EXTI2_3_IRQn, 3, 0);
  HAL_NVIC_EnableIRQ(EXTI2_3_IRQn);

}

/* USER CODE BEGIN 2 */

/* USER CODE END 2 */

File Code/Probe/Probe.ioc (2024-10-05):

#MicroXplorer Configuration settings - do not modify
ADC1.Channel-0\#ChannelRegularConversion=ADC_CHANNEL_0
ADC1.ContinuousConvMode=DISABLE
ADC1.DiscontinuousConvMode=ENABLE
ADC1.IPParameters=Rank-0\#ChannelRegularConversion,Channel-0\#ChannelRegularConversion,SamplingTime-0\#ChannelRegularConversion,NbrOfConversionFlag,master,ContinuousConvMode,ScanConvMode,DiscontinuousConvMode
ADC1.NbrOfConversionFlag=1
ADC1.Rank-0\#ChannelRegularConversion=1
ADC1.SamplingTime-0\#ChannelRegularConversion=ADC_SAMPLETIME_3CYCLES
ADC1.ScanConvMode=ENABLE
ADC1.master=1
CAD.formats=
CAD.pinconfig=
CAD.provider=
File.Version=6
GPIO.groupedBy=Group By Peripherals
KeepUserPlacement=false
Mcu.CPN=STM32F401RCT6TR
Mcu.Family=STM32F4
Mcu.IP0=ADC1
Mcu.IP1=I2C1
Mcu.IP2=NVIC
Mcu.IP3=RCC
Mcu.IP4=SYS
Mcu.IP5=TIM10
Mcu.IP6=USART1
Mcu.IP7=USART6
Mcu.IPNb=8
Mcu.Name=STM32F401R(B-C)Tx
Mcu.Package=LQFP64
Mcu.Pin0=PC13-ANTI_TAMP
Mcu.Pin1=PC14-OSC32_IN
Mcu.Pin10=PA3
Mcu.Pin11=PA4
Mcu.Pin12=PA5
Mcu.Pin13=PA6
Mcu.Pin14=PA7
Mcu.Pin15=PC4
Mcu.Pin16=PC5
Mcu.Pin17=PB0
Mcu.Pin18=PB1
Mcu.Pin19=PB2
Mcu.Pin2=PC15-OSC32_OUT
Mcu.Pin20=PC6
Mcu.Pin21=PC7
Mcu.Pin22=PC8
Mcu.Pin23=PC9
Mcu.Pin24=PA11
Mcu.Pin25=PA12
Mcu.Pin26=PA13
Mcu.Pin27=PA14
Mcu.Pin28=PC10
Mcu.Pin29=PC11
Mcu.Pin3=PC0
Mcu.Pin30=PC12
Mcu.Pin31=PB6
Mcu.Pin32=PB7
Mcu.Pin33=PB8
Mcu.Pin34=PB9
Mcu.Pin35=VP_SYS_VS_Systick
Mcu.Pin36=VP_TIM10_VS_ClockSourceINT
Mcu.Pin4=PC1
Mcu.Pin5=PC2
Mcu.Pin6=PC3
Mcu.Pin7=PA0-WKUP
Mcu.Pin8=PA1
Mcu.Pin9=PA2
Mcu.PinsNb=37
Mcu.ThirdPartyNb=0
Mcu.UserConstants=
Mcu.UserName=STM32F401RCTx
MxCube.Version=6.10.0
MxDb.Version=DB.6.0.100
NVIC.BusFault_IRQn=true\:0\:0\:false\:false\:true\:false\:false\:false
NVIC.DebugMonitor_IRQn=true\:0\:0\:false\:false\:true\:false\:false\:false
NVIC.ForceEnableDMAVector=true
NVIC.HardFault_IRQn=true\:0\:0\:false\:false\:true\:false\:false\:false
NVIC.MemoryManagement_IRQn=true\:0\:0\:false\:false\:true\:false\:false\:false
NVIC.NonMaskableInt_IRQn=true\:0\:0\:false\:false\:true\:false\:false\:false
NVIC.PendSV_IRQn=true\:0\:0\:false\:false\:true\:false\:false\:false
NVIC.PriorityGroup=NVIC_PRIORITYGROUP_4
NVIC.SVCall_IRQn=true\:0\:0\:false\:false\:true\:false\:false\:false
NVIC.SysTick_IRQn=true\:15\:0\:false\:false\:true\:false\:true\:false
NVIC.USART1_IRQn=true\:0\:0\:false\:true\:true\:1\:true\:true\:true
NVIC.USART6_IRQn=true\:0\:0\:false\:true\:true\:2\:true\:true\:true
NVIC.UsageFault_IRQn=true\:0\:0\:false\:false\:true\:false\:false\:false
PA0-WKUP.GPIOParameters=GPIO_Label
PA0-WKUP.GPIO_Label=Unbuff_DAC
PA0-WKUP.Locked=true
PA0-WKUP.Signal=ADCx_IN0
PA1.GPIOParameters=GPIO_Label
PA1.GPIO_Label=DAC
PA1.Locked=true
PA1.Signal=ADCx_IN1
PA11.Mode=Asynchronous
PA11.Signal=USART6_TX
PA12.Mode=Asynchronous
PA12.Signal=USART6_RX
PA13.Mode=Serial_Wire
PA13.Signal=SYS_JTMS-SWDIO
PA14.Mode=Serial_Wire
PA14.Signal=SYS_JTCK-SWCLK
PA2.GPIOParameters=GPIO_Label
PA2.GPIO_Label=Amp
PA2.Locked=true
PA2.Signal=ADCx_IN2
PA3.GPIOParameters=GPIO_Label
PA3.GPIO_Label=Signal
PA3.Locked=true
PA3.Signal=ADCx_IN3
PA4.GPIOParameters=GPIO_Label
PA4.GPIO_Label=Au1
PA4.Locked=true
PA4.Signal=ADCx_IN4
PA5.GPIOParameters=GPIO_Label
PA5.GPIO_Label=Au2
PA5.Locked=true
PA5.Signal=ADCx_IN5
PA6.GPIOParameters=GPIO_Label
PA6.GPIO_Label=Ti1
PA6.Locked=true
PA6.Signal=ADCx_IN6
PA7.GPIOParameters=GPIO_Label
PA7.GPIO_Label=Ti2
PA7.Locked=true
PA7.Signal=ADCx_IN7
PB0.GPIOParameters=GPIO_Label
PB0.GPIO_Label=Calib
PB0.Signal=ADCx_IN8
PB1.GPIOParameters=GPIO_Label
PB1.GPIO_Label=LED_Red
PB1.Locked=true
PB1.Signal=GPIO_Output
PB2.GPIOParameters=GPIO_Label
PB2.GPIO_Label=LED_Green
PB2.Locked=true
PB2.Signal=GPIO_Output
PB6.GPIOParameters=GPIO_Label
PB6.GPIO_Label=RS485_UART
PB6.Locked=true
PB6.Mode=Half_duplex(single_wire_mode)
PB6.Signal=USART1_TX
PB7.GPIOParameters=GPIO_Label
PB7.GPIO_Label=RS485_DE
PB7.Locked=true
PB7.Signal=GPIO_Output
PB8.Mode=I2C
PB8.Signal=I2C1_SCL
PB9.Mode=I2C
PB9.Signal=I2C1_SDA
PC0.GPIOParameters=GPIO_Label
PC0.GPIO_Label=SW_R1_100
PC0.Locked=true
PC0.Signal=GPIO_Output
PC1.GPIOParameters=GPIO_Label
PC1.GPIO_Label=SW_R1_1k
PC1.Locked=true
PC1.Signal=GPIO_Output
PC10.GPIOParameters=GPIO_Label
PC10.GPIO_Label=SW_Ti1_GND
PC10.Locked=true
PC10.Signal=GPIO_Output
PC11.GPIOParameters=GPIO_Label
PC11.GPIO_Label=SW_Ti2_GND
PC11.Locked=true
PC11.Signal=GPIO_Output
PC12.GPIOParameters=GPIO_Label
PC12.GPIO_Label=SW_Shield1_V
PC12.Locked=true
PC12.Signal=GPIO_Output
PC13-ANTI_TAMP.GPIOParameters=GPIO_Label
PC13-ANTI_TAMP.GPIO_Label=SW_Shield2_V
PC13-ANTI_TAMP.Locked=true
PC13-ANTI_TAMP.Signal=GPIO_Output
PC14-OSC32_IN.GPIOParameters=GPIO_Label
PC14-OSC32_IN.GPIO_Label=SW_Shield1_GND
PC14-OSC32_IN.Locked=true
PC14-OSC32_IN.Signal=GPIO_Output
PC15-OSC32_OUT.GPIOParameters=GPIO_Label
PC15-OSC32_OUT.GPIO_Label=SW_Shield2_GND
PC15-OSC32_OUT.Locked=true
PC15-OSC32_OUT.Signal=GPIO_Output
PC2.GPIOParameters=GPIO_Label
PC2.GPIO_Label=SW_R1_10k
PC2.Locked=true
PC2.Signal=GPIO_Output
PC3.GPIOParameters=GPIO_Label
PC3.GPIO_Label=SW_R1_Calib
PC3.Locked=true
PC3.Signal=GPIO_Output
PC4.GPIOParameters=GPIO_Label
PC4.GPIO_Label=SW_R1_Au1
PC4.Locked=true
PC4.Signal=GPIO_Output
PC5.GPIOParameters=GPIO_Label
PC5.GPIO_Label=SW_R1_Au2
PC5.Locked=true
PC5.Signal=GPIO_Output
PC6.GPIOParameters=GPIO_Label
PC6.GPIO_Label=SW_R1_Ti1
PC6.Locked=true
PC6.Signal=GPIO_Output
PC7.GPIOParameters=GPIO_Label
PC7.GPIO_Label=SW_R1_Ti2
PC7.Locked=true
PC7.Signal=GPIO_Output
PC8.GPIOParameters=GPIO_Label
PC8.GPIO_Label=SW_Au1_GND
PC8.Locked=true
PC8.Signal=GPIO_Output
PC9.GPIOParameters=GPIO_Label
PC9.GPIO_Label=SW_Au2_GND
PC9.Locked=true
PC9.Signal=GPIO_Output
PinOutPanel.RotationAngle=0
ProjectManager.AskForMigrate=true
ProjectManager.BackupPrevious=false
ProjectManager.CompilerOptimize=6
ProjectManager.ComputerToolchain=false
ProjectManager.CoupleFile=true
ProjectManager.CustomerFirmwarePackage=
ProjectManager.DefaultFWLocation=true
ProjectManager.DeletePrevious=true
ProjectManager.DeviceId=STM32F401RCTx
ProjectManager.FirmwarePackage=STM32Cube FW_F4 V1.28.0
ProjectManager.FreePins=true
ProjectManager.HalAssertFull=false
ProjectManager.HeapSize=0x200
ProjectManager.KeepUserCode=true
ProjectManager.LastFirmware=false
ProjectManager.LibraryCopy=0
ProjectManager.MainLocation=Core/Src
ProjectManager.NoMain=false
ProjectManager.PreviousToolchain=
ProjectManager.ProjectBuild=false
ProjectManager.ProjectFileName=Probe.ioc
ProjectManager.ProjectName=Probe
ProjectManager.ProjectStructure=
ProjectManager.RegisterCallBack=
ProjectManager.StackSize=0x400
ProjectManager.TargetToolchain=Makefile
ProjectManager.ToolChainLocation=
ProjectManager.UAScriptAfterPath=
ProjectManager.UAScriptBeforePath=
ProjectManager.UnderRoot=false
ProjectManager.functionlistsort=1-SystemClock_Config-RCC-false-HAL-false,2-MX_GPIO_Init-GPIO-false-HAL-true,3-MX_ADC1_Init-ADC1-false-HAL-true,4-MX_I2C1_Init-I2C1-false-HAL-true,5-MX_USART1_UART_Init-USART1-false-HAL-true,6-MX_USART6_UART_Init-USART6-false-HAL-true,7-MX_TIM10_Init-TIM10-false-HAL-true
RCC.AHBFreq_Value=16000000
RCC.APB1Freq_Value=16000000
RCC.APB2Freq_Value=16000000
RCC.CortexFreq_Value=16000000
RCC.HSE_VALUE=25000000
RCC.HSI_VALUE=16000000
RCC.I2SClocksFreq_Value=96000000
RCC.IPParameters=AHBFreq_Value,APB1Freq_Value,APB2Freq_Value,CortexFreq_Value,HSE_VALUE,HSI_VALUE,I2SClocksFreq_Value,LSE_VALUE,LSI_VALUE,PLLCLKFreq_Value,PLLQCLKFreq_Value,RTCFreq_Value,RTCHSEDivFreq_Value,SYSCLKFreq_VALUE,VCOI2SOutputFreq_Value,VCOInputFreq_Value,VCOOutputFreq_Value,VcooutputI2S
RCC.LSE_VALUE=32768
RCC.LSI_VALUE=32000
RCC.PLLCLKFreq_Value=96000000
RCC.PLLQCLKFreq_Value=48000000
RCC.RTCFreq_Value=32000
RCC.RTCHSEDivFreq_Value=12500000
RCC.SYSCLKFreq_VALUE=16000000
RCC.VCOI2SOutputFreq_Value=192000000
RCC.VCOInputFreq_Value=1000000
RCC.VCOOutputFreq_Value=192000000
RCC.VcooutputI2S=96000000
SH.ADCx_IN0.0=ADC1_IN0,IN0
SH.ADCx_IN0.ConfNb=1
SH.ADCx_IN1.0=ADC1_IN1,IN1
SH.ADCx_IN1.ConfNb=1
SH.ADCx_IN2.0=ADC1_IN2,IN2
SH.ADCx_IN2.ConfNb=1
SH.ADCx_IN3.0=ADC1_IN3,IN3
SH.ADCx_IN3.ConfNb=1
SH.ADCx_IN4.0=ADC1_IN4,IN4
SH.ADCx_IN4.ConfNb=1
SH.ADCx_IN5.0=ADC1_IN5,IN5
SH.ADCx_IN5.ConfNb=1
SH.ADCx_IN6.0=ADC1_IN6,IN6
SH.ADCx_IN6.ConfNb=1
SH.ADCx_IN7.0=ADC1_IN7,IN7
SH.ADCx_IN7.ConfNb=1
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

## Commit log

2024-08-10 started pcbs
    [GoldElectrode.kicad_pcb, GoldElectrode.kicad_sch, Probe.kicad_pcb, Probe.kicad_sch]
2024-08-19 pcb work
    [BOM.csv, BOM.xlsx, CPL.xlsx, Controller.kicad_pcb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]
2024-08-28 kicad changes
    [BOM.csv, BOM.xlsx, CPL.xlsx, Controller BOM.xlsx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]
2024-09-10 heading for lit review
    [BOM.csv, Controller BOM.xlsx, Controller CPL.xlsx, Controller-B_Cu.gbl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]
2024-09-27 controller test code
    [CircuitDiagrams.kicad_pcb, CircuitDiagrams.kicad_sch, ResistanceMeasurement.kicad_sch]
2024-10-02 temp and depth sensor
2024-10-05 board to board coms work
2024-10-08 testing phase 1 started
    [Testing.xlsx]
2024-10-10 testing phase 1 complete
    [Testing.xlsx]
2024-10-10 report writing
    [CircuitDiagrams.kicad_pcb, CircuitDiagrams.kicad_sch, ResistanceMeasurement.kicad_sch, Testing.xlsx]
2024-10-15 prepping for salt water tests
    [Testing.xlsx, switch_cap.FCStd]
2024-10-17 more tests
    [Testing.xlsx, switch_cap.stl]
2024-10-20 grammarly intro-theory
    [Testing.xlsx]
2024-10-22 design and implementation grammarly
    [Testing.xlsx]
2024-10-23 testing complete
    [GoldElectrode.kicad_pcb, Testing.xlsx]
2024-10-23 last graphs
    [Testing.xlsx]
2024-10-24 finishing touches
    [Testing.xlsx]
